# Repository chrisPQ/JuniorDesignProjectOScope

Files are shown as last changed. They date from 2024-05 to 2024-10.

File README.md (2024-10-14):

# JuniorDesignProjectOScope
Teensy program to run oscilloscope and output to screen

Video Overview: https://www.youtube.com/watch?v=Kpc6_z2Lm2U&ab_channel=MarshallG

Showcase Page: https://eecs.engineering.oregonstate.edu/project-showcase/projects/?id=eiNZnlOKVvULkvkf

Design Problem:
The design problem was to create a 2-channel oscilloscope. The scope needed to have voltage
scaling, time scaling, and trigger capabilities. The system also needs to have AC/DC coupling
modes, and a responsive interface.

Design process: The first step in our design process was to do some preliminary research to
see what it was we would need to accomplish the requirements. This included taking into
account the different choices of hardware we could use. We initially considered this project
based on a field programmable gate array due to the high sampling requirement that were
initially on the project instructions. After that requirement was removed, we went with our
second option, which was a Teensy 4.0 microcontroller board. We went with this option because
it is relatively inexpensive (especially compared to an FPGA), but it is still very fast with a clock
speed of 600 megahertz.

Our next big hurdle was figuring out how to implement the input circuitry. Since we decided our
input signal range was 0-20 volts peak to peak, and our microcontroller could only handle a
range of 0-3.3 volts, we had to adjust the signal to be able to measure it. We worked together on
designing the circuit and simulating the results in LTspice. We then soldered it to a protoboard
and experimented with the circuit in the lab. Our team had to work together to troubleshoot the
circuit and adjust the component values to perform as expected.

Although our whole system was split into individual blocks, we had to work together very closely
to ensure our systems would work as expected. For example, the input conditioning block has to
take voltage from the power supply block. Then the signal conversion and processing block had
to take input from the signal conditioning block.Communication about these individual tasks
made our system integration go smoother as the different pieces meshed together well.

Once all the circuit prototypes were designed and tested, we put them onto a PCB. We worked
together to peer review the PCB to ensure it would work correctly. Once the board arrived, we
used tools in the lab such as the oven and soldering irons to assemble the components onto the
board. This phase was a challenge as we included some very small surface mount parts in our
design. One challenge we had at this stage was that we had some slight mistakes in the PCB.
The pin header where the microcontroller was supposed to be ended up being one pin too
short. We fixed this by making an adapter board that mapped the pins of the MCU (expected
one two that we didn’t need) to a set of pin headers that was the correct number for the footprint
on the PCB.

We finished the process by working on our embedded software to control the device. This was a
challenge because it included meshing together code covering many different tasks, all of which
had challenges of their own.

Timeline:
April 19th: Engineering requirments devised.
April 26th: First block documentation.
May 1st: First Block verification.
May 10th: Second Block documentation
May 15th: Second block verification.
May 31st: System Verification.
June 5th: Demo of final project.

Takeaways:
Over the course of this project we learned about working on a complex project with a tight
deadline. This taught us many lessons of project management and how to focus on prioritizing
the important parts when it comes to developing electronics projects. Specifically we learned the
importance of researching and simulation methods before diving into them. While this may
seem restraining at first, it is a method that saves time and money in the long run because
things are more likely to work the first time around. We also learned many things about specific
technologies. Using direct memory access and interrupts to enhance the performance speed of
our microcontroller were concepts that required us to research and access data that wasn’t as
accessible as things we had worked on in the past.

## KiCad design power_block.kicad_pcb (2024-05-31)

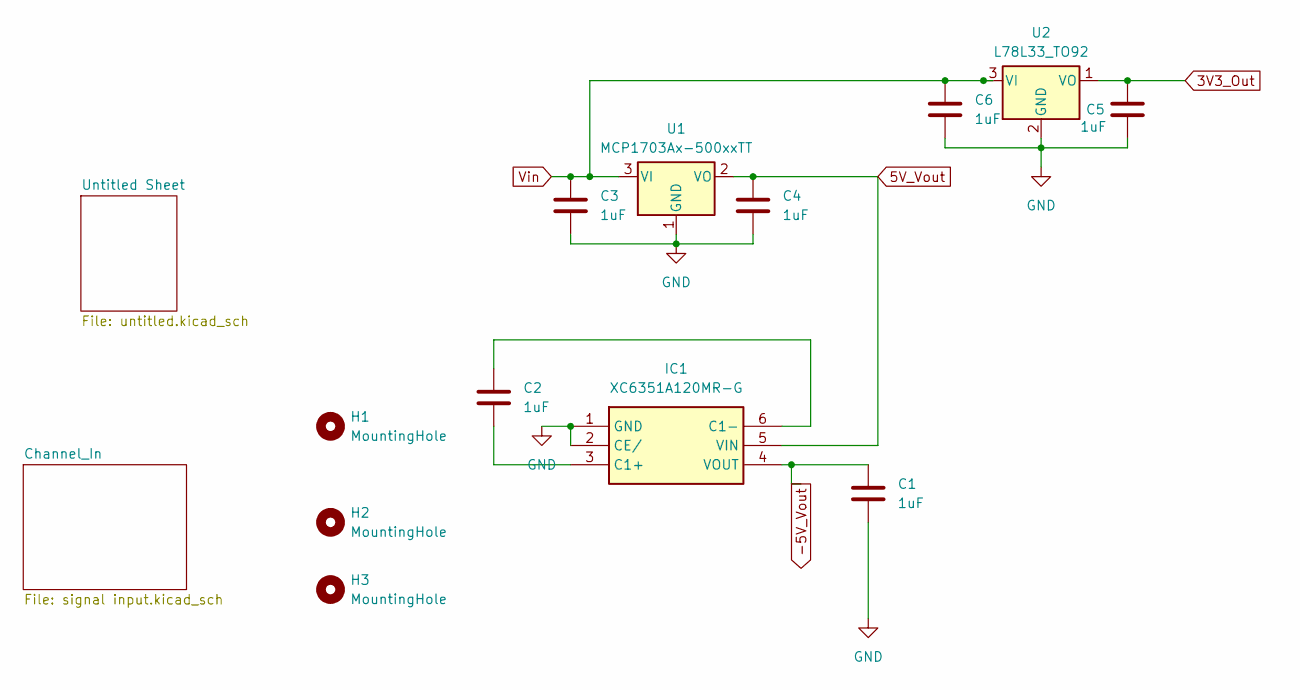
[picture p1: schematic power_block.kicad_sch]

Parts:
C1, C2, C3, C4, C5, C6: 1uF; C_0603_1608Metric_Pad1.08x0.95mm_HandSolder
H1, H2, H3: MountingHole; MountingHole_3.2mm_M3
IC1: XC6351A120MR-G; SOT-23-6; Mouser Part Number 865-XC6351A120MR-G
U1: MCP1703Ax-500xxTT; SOT-23
U2: L78L33_TO92; TO-92_Inline_Wide

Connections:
3V3_Out: C5.2, U2.1 (VO); also elsewhere on the board
5V_Vout: C4.1, IC1.5 (VIN), U1.2 (VO); also elsewhere on the board
-5V_Vout: C1.1, IC1.4 (VOUT); also elsewhere on the board
GND: C1.2, C3.2, C4.2, C5.1, C6.2, IC1.1 (GND), IC1.2 (CE/), U1.1 (GND), U2.2 (GND); also elsewhere on the board
unnamed: C2.2, IC1.3 (C1+)
unnamed: C2.1, IC1.6 (C1-)
Vin: C3.1, C6.1, U1.3 (VI), U2.3 (VI); also elsewhere on the board

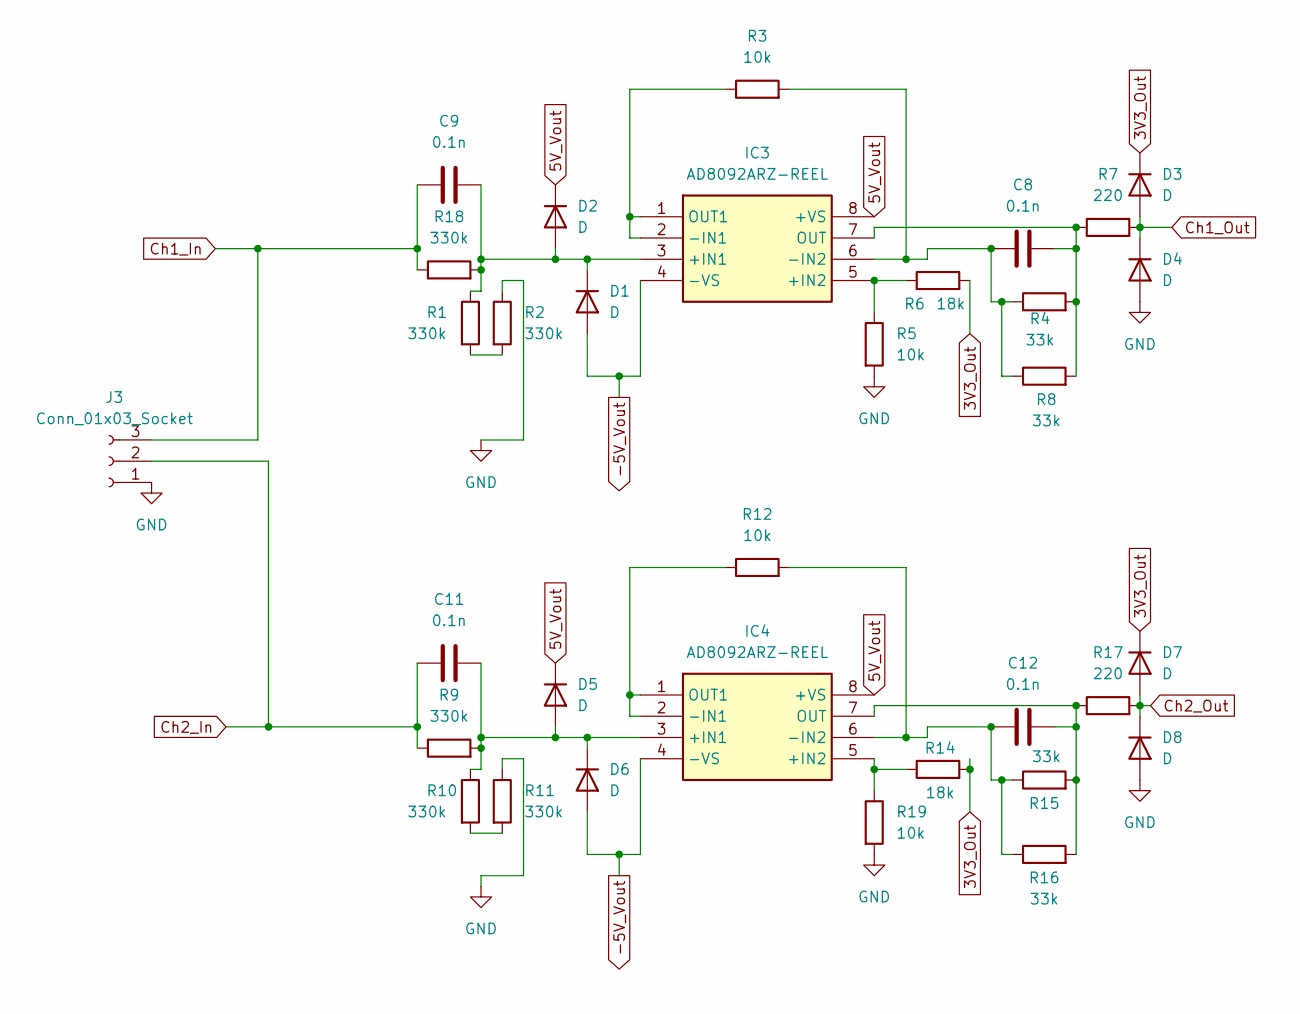
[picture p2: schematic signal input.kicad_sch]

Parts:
C8, C9, C11, C12: 0.1n; C_1206_3216Metric_Pad1.33x1.80mm_HandSolder
D1, D2, D3, D4, D5, D6, D7, D8: D; D_MiniMELF
IC3, IC4: AD8092ARZ-REEL; SOIC-8_3.9x4.9mm_P1.27mm; Mouser Part Number 584-AD8092ARZ-R
J3: Conn_01x03_Socket; JST_EH_B3B-EH-A_1x03_P2.50mm_Vertical
R1, R2, R9, R10, R11, R18: 330k; R_0805_2012Metric_Pad1.20x1.40mm_HandSolder
R3, R5, R12, R19: 10k; R_0805_2012Metric_Pad1.20x1.40mm_HandSolder
R4, R8, R15, R16: 33k; R_0603_1608Metric_Pad0.98x0.95mm_HandSolder
R6, R14: 18k; R_0603_1608Metric_Pad0.98x0.95mm_HandSolder
R7, R17: 220; R_1206_3216Metric_Pad1.30x1.75mm_HandSolder

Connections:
3V3_Out: D3.1 (K), D7.1 (K), R6.2, R14.2; also elsewhere on the board
5V_Vout: D2.1 (K), D5.1 (K), IC3.8 (+VS), IC4.8 (+VS); also elsewhere on the board
-5V_Vout: D1.2 (A), D6.2 (A), IC3.4 (-VS), IC4.4 (-VS); also elsewhere on the board
Ch1_In: C9.1, J3.3, R18.1
Ch1_Out: D3.2 (A), D4.1 (K), R7.2; also elsewhere on the board
Ch2_In: C11.1, J3.2, R9.1
Ch2_Out: D7.2 (A), D8.1 (K), R17.2; also elsewhere on the board
GND: D4.2 (A), D8.2 (A), J3.1, R2.1, R5.2, R11.1, R19.2; also elsewhere on the board
unnamed: C9.2, D1.1 (K), D2.2 (A), IC3.3 (+IN1), R1.1, R18.2
unnamed: C11.2, D5.2 (A), D6.1 (K), IC4.3 (+IN1), R9.2, R10.1
unnamed: IC3.5 (+IN2), R5.1, R6.1
unnamed: IC3.1 (OUT1), IC3.2 (-IN1), R3.1
unnamed: C8.1, IC3.6 (-IN2), R3.2, R4.1, R8.1
unnamed: C8.2, IC3.7 (OUT), R4.2, R7.1, R8.2
unnamed: IC4.5 (+IN2), R14.1, R19.1
unnamed: IC4.1 (OUT1), IC4.2 (-IN1), R12.1
unnamed: C12.1, IC4.6 (-IN2), R12.2, R15.1, R16.1
unnamed: C12.2, IC4.7 (OUT), R15.2, R16.2, R17.1
unnamed: R1.2, R2.2
unnamed: R10.2, R11.2

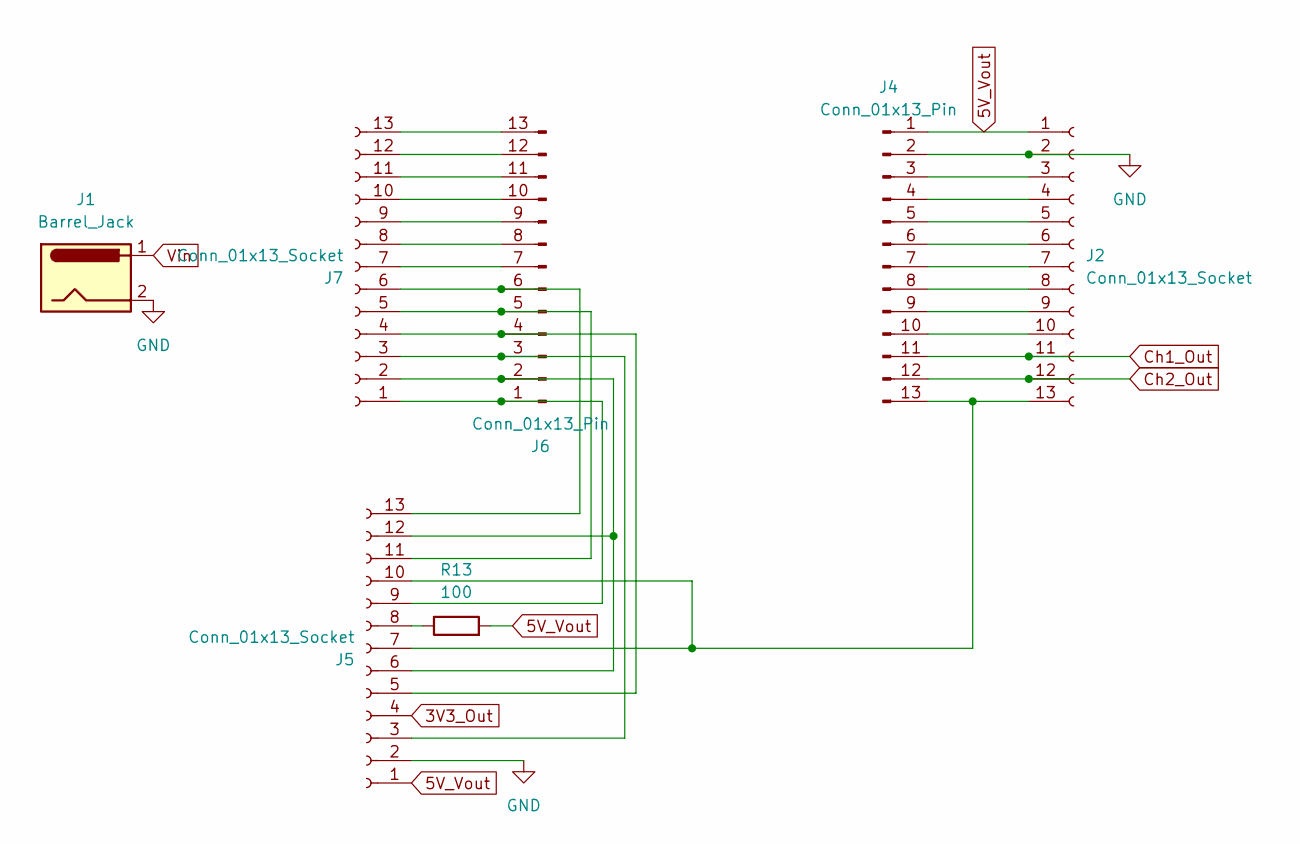
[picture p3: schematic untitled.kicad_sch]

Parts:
J1: Barrel_Jack; BarrelJack_GCT_DCJ200-10-A_Horizontal
J2, J5, J7: Conn_01x13_Socket; PinHeader_1x13_P2.54mm_Vertical
J4, J6: Conn_01x13_Pin; PinHeader_1x13_P2.54mm_Vertical
R13: 100; R_Axial_DIN0204_L3.6mm_D1.6mm_P7.62mm_Horizontal

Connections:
3V3_Out: J5.4; also elsewhere on the board
5V_Vout: J2.1, J4.1, J5.1, R13.2; also elsewhere on the board
Ch1_Out: J2.11, J4.11; also elsewhere on the board
Ch2_Out: J2.12, J4.12; also elsewhere on the board
GND: J1.2, J2.2, J4.2, J5.2; also elsewhere on the board
unnamed: J2.3, J4.3
unnamed: J2.4, J4.4
unnamed: J2.5, J4.5
unnamed: J2.6, J4.6
unnamed: J2.7, J4.7
unnamed: J2.8, J4.8
unnamed: J2.9, J4.9
unnamed: J2.10, J4.10
unnamed: J2.13, J4.13, J5.7, J5.10
unnamed: J5.3, J6.3, J7.3
unnamed: J5.5, J6.4, J7.4
unnamed: J5.8, R13.1
unnamed: J5.9, J6.1, J7.1
unnamed: J5.11, J6.5, J7.5
unnamed: J5.6, J5.12, J6.2, J7.2
unnamed: J5.13, J6.6, J7.6
unnamed: J6.7, J7.7
unnamed: J6.8, J7.8
unnamed: J6.9, J7.9
unnamed: J6.10, J7.10
unnamed: J6.11, J7.11
unnamed: J6.12, J7.12
unnamed: J6.13, J7.13
Vin: J1.1; also elsewhere on the board

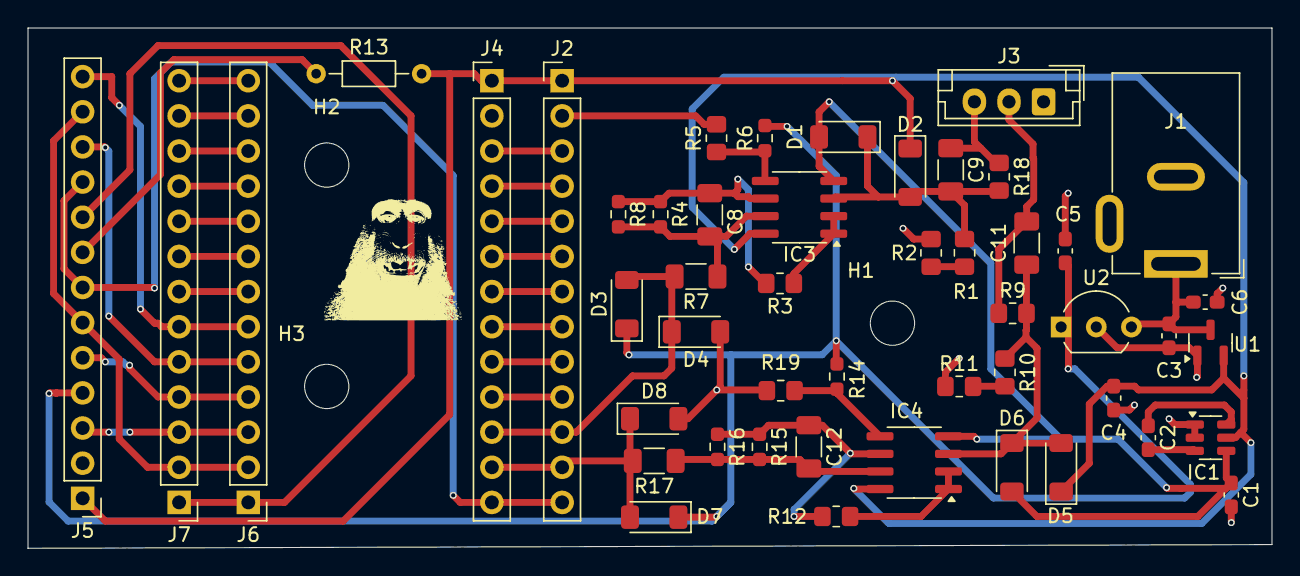
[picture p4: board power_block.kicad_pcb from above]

Board: 2 copper layers, 89.9 x 37.6 mm, 52 parts (0 on the bottom side), 46 nets.

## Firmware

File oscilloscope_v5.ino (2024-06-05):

#include "SPI.h"
#include "Adafruit_GFX.h"
#include "Adafruit_ILI9341.h"
#include <ADC.h>
#include <AnalogBufferDMA.h>
#include <DMAChannel.h>
#include <Encoder.h>

// For the Adafruit shield, these are the default.
#define TFT_DC 9
#define TFT_CS 10

#define COLUMNS 15
#define ROWS 11

// Vertical scale settings
const float vScale_min = 2.0;  // 2 volts per division
const float vScale_max = 5.0;  // 5 volts per division

float vScale = 2.0;  // Start at the minimum vertical scale
volatile long hScale = 1;
long prev_h;
long prev_v;

// Variables to store the last time the button state changed
unsigned long buttonPressStartTime = 0;
unsigned long buttonReleaseStartTime = 0;

// Time thresholds in milliseconds
const unsigned long pressThreshold = 1000;    // Time the button must be held to edit vScale
const unsigned long releaseThreshold = 1000;  // Time the button must be released to edit hScale

// Variable to track the current state of the button
bool buttonWasPressed = false;
Adafruit_ILI9341 tft = Adafruit_ILI9341(TFT_CS, TFT_DC, 11, 13, 6, 12);

#if defined(ADC_USE_DMA) && defined(ADC_USE_TIMER)

const int readPin_adc_0 = 14;
const int readPin_adc_1 = 15;

ADC *adc = new ADC();

const uint32_t buffer_size = 1600;
DMAMEM static volatile uint16_t __attribute__((aligned(32))) dma_adc_buff1[buffer_size];
DMAMEM static volatile uint16_t __attribute__((aligned(32))) dma_adc_buff2[buffer_size];
AnalogBufferDMA abdma1(dma_adc_buff1, buffer_size, dma_adc_buff2, buffer_size);

DMAMEM static volatile uint16_t __attribute__((aligned(32))) dma_adc_buff2_1[buffer_size];
DMAMEM static volatile uint16_t __attribute__((aligned(32))) dma_adc_buff2_2[buffer_size];
AnalogBufferDMA abdma2(dma_adc_buff2_1, buffer_size, dma_adc_buff2_2, buffer_size);

elapsedMillis elapsed_sinc_last_display;

Encoder trigger_Enc(21, 22);
int triggerIndex = 0;
//Encoder scale_Enc(19, 20);
#define scale_select 18

int h_scale_min = 1;
int h_scale_max = 200;

double trigger;
bool trig_flag = false;

unsigned long int last = 0;
bool first_print = true;
volatile uint16_t *prev_data;

#define chA 19
#define chB 20
int aState;
int aLastState;
float hcounter = 1;
float vcounter = 1;
#define scale_select 18
volatile int buttonState = 0;


//Variables for low-pass filtering
const float alpha = 0.8;            //<- Making this valu lower intensifies filtering effect and vice-versa
double data_filtered[] = { 0, 0 };  // data_filtered[n] is where the most recent filtered value can be accessed
const int n = 1;


void setup() {
  pinMode(scale_select, INPUT);
  pinMode(chA, INPUT);
  pinMode(chB, INPUT);

  aLastState = digitalRead(chA);
  attachInterrupt(digitalPinToInterrupt(chA), update_encoder, CHANGE);
  Serial.begin(1000000);
  while (!Serial && millis() < 5000)
    ;

  pinMode(LED_BUILTIN, OUTPUT);
  pinMode(readPin_adc_0, INPUT_DISABLE);
  pinMode(readPin_adc_1, INPUT_DISABLE);

  adc->adc0->setAveraging(1);
  adc->adc0->setResolution(10);
  adc->adc1->setAveraging(80);
  adc->adc1->setResolution(10);

  abdma1.init(adc, ADC_0);
  abdma1.userData(0);
  abdma2.init(adc, ADC_1);
  abdma2.userData(0);

  adc->adc0->startSingleRead(readPin_adc_0);
  adc->adc0->startTimer(500000);
  adc->adc1->startSingleRead(readPin_adc_1);
  adc->adc1->startTimer(500000);

  tft.begin();
  tft.setRotation(1);
  tft.fillScreen(ILI9341_BLACK);  // Clear the screen once
  drawFrame();
}

void loop() {
  buttonState = digitalRead(scale_select);  // Read button state
  drawFrame();                              // initialize blank frame
  if (abdma1.interrupted() && abdma2.interrupted()) {
    ProcessAnalogData(&abdma1, 0);
    ProcessAnalogData(&abdma2, 1);
    elapsed_sinc_last_display = 0;
  }
  if (abdma1.interrupted()) {
    ProcessAnalogData(&abdma1, 0);
    elapsed_sinc_last_display = 0;
  }
  if (abdma2.interrupted()) {
    ProcessAnalogData(&abdma2, 1);
    elapsed_sinc_last_display = 0;
  }
}

void ProcessAnalogData(AnalogBufferDMA *pabdma, int8_t adc_num1) {
  trigger = trigger_Enc.read();
  hScale = clamp(hScale, h_scale_min, h_scale_max);

  volatile uint16_t *pbuffer = pabdma->bufferLastISRFilled();
  volatile uint16_t *end_pbuffer = pbuffer + pabdma->bufferCountLastISRFilled();

  if ((uint32_t)pbuffer >= 0x20200000u) {
    arm_dcache_delete((void *)pbuffer, sizeof(dma_adc_buff1));
  }

  int16_t x = 0;

  tft.drawFastHLine(0, trigger, 280, ILI9341_YELLOW);  // draw trigger line
  volatile uint16_t triggerIndex = get_trigger_index(pabdma);
  float y_prev;
  float x_prev;
if(trig_flag){
    for (volatile uint16_t *i = pbuffer+triggerIndex - 160; i < pbuffer+triggerIndex - 160 + 320; i++) {
    float y1 = ((((*i * 3.3) / 1024) / 1.65));
    float y2 = (y1 - 1.17) * 20 * (-1);
    float y3 = mapVoltageToRange(y2);
    if (adc_num1 == 0) {
      if (!first_print) {
        tft.drawLine(x_prev, y_prev, x * 100 / hScale, y3, ILI9341_GREEN);

      } else {
        // tft.drawLine(x_prev, y_prev, x * 100 / hScale, y3, ILI9341_GREEN);
      }
    } else {
      if (!first_print) {
        tft.drawLine(x_prev, y_prev, x * 100 / hScale, y3, ILI9341_BLUE);
      } else {
        tft.drawLine(x_prev, y_prev, x * 100 / hScale, y3, ILI9341_BLUE);
      }
    }
    x_prev = x * 100 / hScale;
    x++;
    y_prev = y3;
  }
}else{
  for (volatile uint16_t *i = pbuffer; i < pbuffer + 320; i++) {
    float y1 = ((((*i * 3.3) / 1024) / 1.65));
    float y2 = (y1 - 1.17) * 20 * (-1);
    float y3 = mapVoltageToRange(y2);
    if (adc_num1 == 0) {
      if (!first_print) {
        tft.drawLine(x_prev, y_prev, x * 100 / hScale, y3, ILI9341_GREEN);

      } else {
        // tft.drawLine(x_prev, y_prev, x * 100 / hScale, y3, ILI9341_GREEN);
      }
    } else {
      if (!first_print) {
        tft.drawLine(x_prev, y_prev, x * 100 / hScale, y3, ILI9341_BLUE);
      } else {
        tft.drawLine(x_prev, y_prev, x * 100 / hScale, y3, ILI9341_BLUE);
      }
    }
    x_prev = x * 100 / hScale;
    x++;
    y_prev = y3;
  }
}
  pabdma->clearInterrupt();

  trig_flag = false;

  first_print = false;
  if (!first_print) {
    prev_data = pbuffer;
  }
  delay(300);
}

void drawFrame() {
  tft.fillRect(0, 0, tft.width(), tft.height(), ILI9341_BLACK);
  // Draw the grid using individual pixels
  for (int16_t i = 0; i < COLUMNS; i++) {
    for (int16_t j = 0; j < ROWS; j++) {
      for (int16_t k = -2; k <= 2; k++) {
        tft.drawPixel(20 * i, j * 20 + k, ILI9341_WHITE);  // Vertical pixels
        tft.drawPixel(20 * i + k, j * 20, ILI9341_WHITE);  // Horizontal pixels
      }
    }
  }

  // Draw the scale indicators
  tft.setCursor(0, ROWS * 20);
  tft.setTextSize(1);
  tft.setTextColor(ILI9341_YELLOW);
  tft.print("V Scale: ");
  tft.print(vScale);
  tft.println(" V/div");
  tft.setCursor(100, ROWS * 20);
  tft.print("H Scale: ");
  tft.println(hScale);
}

#else
void setup() {}
void loop() {}
#endif

int16_t clamp(int16_t val, int min, int max) {
  if (val < min) {
    val = min;
  }

  if (val > max) {
    val = max;
  }
  return val;
}

volatile uint16_t get_trigger_index(AnalogBufferDMA *dma_buffer_in) {
  volatile uint16_t *screenBuffer = dma_buffer_in->bufferLastISRFilled();
  volatile uint16_t *end_pbuffer = screenBuffer + dma_buffer_in->bufferCountLastISRFilled();
  volatile uint16_t *triggerIndex = screenBuffer + 140;


  for (volatile uint16_t *i = screenBuffer + 160; i < end_pbuffer - 160; i++) {
    float y1 = ((((*i * 3.3) / 1024) / 1.65));
    float y2 = (y1 - 1.17) * 20 * (-1);
      Serial.print("\nTrigger voltage: ");
  Serial.print(trigger);
  Serial.print("  Current voltage: ");
  Serial.print(y2);
    if (abs(trigger -y2) < 0.5) {
      Serial.print("\n\nTriggered\n\n");

      triggerIndex = i;
      trig_flag = true;
      return triggerIndex;
    }
  }
  trig_flag = false;
  return -1;
}

// Function to map voltage to the desired range and return an integer
int mapVoltageToRange(float voltage) {
  float max = 20.0;
  if (voltage < (-1) * max) voltage = (-1) * max;
  if (voltage > max) voltage = max;
  int max_pixel = 240 - (24 * vScale);
  int min_pixel = 24 * vScale;
  int mappedValue = (int)(((voltage + max) / (2 * max)) * max_pixel) + min_pixel;
  return mappedValue;
}

void update_encoder() {
  int aState = digitalRead(chA);  // Read the "current" state of channel A

  // If the state of channel A has changed, a pulse has occurred
  if (aState != aLastState) {
    // Determine the direction of rotation
    if (digitalRead(chB) != aState) {
      if (buttonState) {
        Serial.print("\nButton pushed! Increment hScale.");
        hScale++;
      } else {
        Serial.print("\nButton not pushed! Increment vScale.");
        vScale++;
      }
    } else {
      if (buttonState) {
        Serial.print("\nButton pushed! Decrement hScale.");
        hScale--;
      } else {
        Serial.print("\nButton not pushed! Decrement vScale.");
        vScale--;
      }
    }
  }
  // Update the last state
  aLastState = aState;
}

double filter_data(float data_in) {
  // if the received serial command tells us to send sensor data, take a measurement from the photodiode,
  // pass it through the lowpass filter, and send it back to the PC/
  //  if (c == send_data) {
  // Retrieve Data


  // Low Pass Filter
  data_filtered[n] = alpha * data_in + (1 - alpha) * data_filtered[n - 1];

  // Store the last filtered data in data_filtered[n-1]
  data_filtered[n - 1] = data_filtered[n];
  return data_filtered[n];
}

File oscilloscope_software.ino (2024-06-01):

#include "SPI.h"
#include "Adafruit_GFX.h"
#include "Adafruit_ILI9341.h"
#include <ADC.h>
#include <AnalogBufferDMA.h>
#include <DMAChannel.h>
#include <Encoder.h>

// For the Adafruit shield, these are the default.
#define TFT_DC 9
#define TFT_CS 10

#define COLUMNS 15
#define ROWS 11

long vScale = 250;
long hScale = 40;

Adafruit_ILI9341 tft = Adafruit_ILI9341(TFT_CS, TFT_DC, 11, 13, 6, 12);

#if defined(ADC_USE_DMA) && defined(ADC_USE_TIMER)

const int readPin_adc_0 = 14;
const int readPin_adc_1 = 15;

ADC *adc = new ADC();

const uint32_t buffer_size = 1000;
DMAMEM static volatile uint16_t __attribute__((aligned(32))) dma_adc_buff1[buffer_size];
DMAMEM static volatile uint16_t __attribute__((aligned(32))) dma_adc_buff2[buffer_size];
AnalogBufferDMA abdma1(dma_adc_buff1, buffer_size, dma_adc_buff2, buffer_size);

DMAMEM static volatile uint16_t __attribute__((aligned(32))) dma_adc_buff2_1[buffer_size];
DMAMEM static volatile uint16_t __attribute__((aligned(32))) dma_adc_buff2_2[buffer_size];
AnalogBufferDMA abdma2(dma_adc_buff2_1, buffer_size, dma_adc_buff2_2, buffer_size);

elapsedMillis elapsed_sinc_last_display;


Encoder trigger_Enc(21, 22);
Encoder scale_Enc(19, 20);
#define scale_select 18

void setup() {
  pinMode(scale_select, INPUT);
  Serial.begin(1000000);
  while (!Serial && millis() < 5000)
    ;

  pinMode(LED_BUILTIN, OUTPUT);
  pinMode(readPin_adc_0, INPUT_DISABLE);
  pinMode(readPin_adc_1, INPUT_DISABLE);

  adc->adc0->setAveraging(1);
  adc->adc0->setResolution(10);
  adc->adc1->setAveraging(1);
  adc->adc1->setResolution(10);

  abdma1.init(adc, ADC_0);
  abdma1.userData(0);
  abdma2.init(adc, ADC_1);
  abdma2.userData(0);

  adc->adc0->startSingleRead(readPin_adc_0);
  adc->adc0->startTimer(500000);
  adc->adc1->startSingleRead(readPin_adc_1);
  adc->adc1->startTimer(500000);

  tft.begin();
  tft.setRotation(1);

  drawFrame();
}

void loop() {
  if (abdma1.interrupted() && abdma2.interrupted()) {
    ProcessAnalogData(&abdma1, 0,&abdma2, 1);
 //   ProcessAnalogData(&abdma2, 1);
    elapsed_sinc_last_display = 0;
  }

  if (elapsed_sinc_last_display > 5000) {
    digitalWriteFast(13, HIGH);
    delay(250);
    digitalWriteFast(13, LOW);
    delay(250);
    digitalWriteFast(13, HIGH);
    delay(250);
    digitalWriteFast(13, LOW);
    elapsed_sinc_last_display = 0;
  }
}

void ProcessAnalogData(AnalogBufferDMA *pabdma, int8_t adc_num1,AnalogBufferDMA *pabdma2, int8_t adc_num2) {
    //long hscale;
    //long vscale
    long trigger_level = trigger_Enc.read();
    if(digitalRead(scale_select)){
     vScale = scale_Enc.read();
    }else{
      hScale = scale_Enc.read();
    }

    Serial.print("\nvscale: ");
    Serial.print(vScale);
    Serial.print(", hscale: ");
    Serial.print(hScale);

      volatile uint16_t *pbuffer2 = pabdma2->bufferLastISRFilled();
  volatile uint16_t *end_pbuffer2 = pbuffer2 + pabdma->bufferCountLastISRFilled();
        
  volatile uint16_t *pbuffer = pabdma->bufferLastISRFilled();
  volatile uint16_t *end_pbuffer = pbuffer + pabdma->bufferCountLastISRFilled();


    if ((uint32_t)pbuffer2 >= 0x20200000u) {
    arm_dcache_delete((void *)pbuffer, sizeof(dma_adc_buff2));
  }


  if ((uint32_t)pbuffer >= 0x20200000u) {
    arm_dcache_delete((void *)pbuffer, sizeof(dma_adc_buff1));
  }



  tft.fillRect(0, 0, tft.width(), tft.height(), ILI9341_BLACK);
  drawFrame();

  int x = 0;
  while (pbuffer < end_pbuffer && x < tft.width()) {
    //Serial.println(*pbuffer);
    int y1 = tft.height() / 2 - (*pbuffer * 10 / vScale);
    int y2 = tft.height() / 2 - (*pbuffer2 * 10 / vScale);
   // if(adc_num == 0){
    tft.drawPixel(x, y1, ILI9341_GREEN);
    tft.drawPixel(x, y2, ILI9341_BLUE);
    //}else{
    //   tft.drawPixel(x, y, ILI9341_BLUE);
    //}
    delayMicroseconds(1000);
    //delay(1);
    //Serial.print("\nx:");
    //Serial.print(x);
    //Serial.print(" , y: ");
    //Serial.print(y);
    pbuffer++;
    pbuffer2++;
    x++;
  }

  pabdma->clearInterrupt();
  pabdma2->clearInterrupt();
}

void drawFrame() {
  tft.fillRect(0, 0, tft.width(), tft.height(), ILI9341_BLACK);
  for (int16_t i = 0; i < COLUMNS; i++) {
    for (int16_t j = 0; j < ROWS; j++) {
      tft.drawFastVLine(20 * i, j * 20 - 2, 5, ILI9341_WHITE);
      tft.drawFastHLine(20 * i - 2, j * 20, 5, ILI9341_WHITE);
    }
  }

  tft.setCursor(0, ROWS * 20);
  tft.setTextSize(1);
  tft.setTextColor(ILI9341_YELLOW);
  tft.print("V Scale: ");
  tft.println(vScale);
  tft.setCursor(100, ROWS * 20);
  tft.print("H Scale: ");
  tft.setCursor(100, ROWS * 20 + 8);
  tft.println(hScale);
}

#else
void setup() {}
void loop() {}
#endif

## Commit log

2024-05-15 Screen Testing Code for Arduino Mega
2024-05-31 KiCAD Files
    [power_block.kicad_pcb, power_block.kicad_sch, signal input.kicad_sch, untitled.kicad_sch]
